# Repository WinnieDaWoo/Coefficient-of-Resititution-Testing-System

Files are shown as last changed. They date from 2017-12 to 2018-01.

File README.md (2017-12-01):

# A Coefficient of Restitution Testing System for Baseballs

The central task of this project was to design and construct a system to reliably and accurately determine the COR of a baseball with a piece of wood as a function of the relative velocity between the two bodies. This system was designed as part of an interdisciplinary one month CAPSTONE project.

An air cannon, optical laser gate, collision tube assembly was created to determine the coefficient of restitution (CoR) between a baseball and a piece of wood as a function of the relative velocity between the two bodies. A PVC compressed air cannon rated for 120 psi accelerated a baseball to speeds nearing 70 mph, and an optical laser gate captured the speed of the baseball before and after a collision with a piece of wood (ash or pine). The collision was facilitated by a collision tube racked at the end of the cannon barrel. Values for COR from baseball to baseball were consistent to within plus or minus 0.4 at various inbound velocities between 20 and 70 mph. The COR appeared to decrease as the inbound velocity increased. However, not enough data were collected to confidently apply a mathematical model to relate the two quantities. The coefficient of determination for two attempted linear fits were 0.59 and 0.78.

by Adam Woo, Dana Wensberg

## Hardware

Here is a list of the selected hardware:

### Speed Gate
| Component | Model | Description | Price |
| --- | --- | --- | --- |
| Microcontroller | [DFRobot Romeo Board](https://www.dfrobot.com/product-844.html) | The Romeo board is a microcontroller based on the ATmega32u4 chip, like the Arduino Leonardo. While the Romeo board was designed for robotics, the only special features used of this board were the built in buttons to control the system. This board was a loan from the Trinity College Engineering Department. | $0 (Retail: ~$35) |
| LCD | [DFR0063](https://www.dfrobot.com/product-135.html) | This I2C 16x2 Arduino LCD Screen is using an I2C communication interface. It means it only needs 4 pins for the LCD display: VCC, GND, SDA, SCL. It will saves at least 4 digital / analog pins on Arduino. This component was a loan from the Trinity College Engineering Department. | $0 (Retail: ~$35) |
| Lasers |  [6x Generic 650nm 5V Diode Lasers](http://amzn.to/2hCx2co) | Any 5V laser could be used for this project. These were chosen because of their small form factor and cheap price. | ~$3.50 |
| Photodiodes | [6x Generic 5MM Photodiode](http://amzn.to/2zOcfr7) | Photodiodes provide a faster response time than photosensitive resistors or transistors. | ~$1.50 |

### Air Cannon
| Component | Part | Description | Price |
| --- | --- | --- | --- |
| Cannon Materials | Schedule 40 PVC | Rated for high psi and inexpensive | ~$20 |
| Adhesives | Oatey PVC Cement | Adhesive rated for 120 psi. This adhesive was a loan from the Trinity College Engineering Department. | ~$0 |
| Quick Release | Irritrol 205TF 1” Glove valve and a Neiko 31112 Air Blow Gun Oversized Trigger | To create the quick release valve, we modified a sprinkler solenoid valve. Instructions can be read in the report | ~$32.50 |
| Testing Surface | Ash Wood | A custom cut block of ash was used as a testing surface to mimic the materials used in baseball bats | ~$10 |
| Pump | Generic Bike Pump | Any bike pump with a standard schrader valve will fit our system | ~$20 |

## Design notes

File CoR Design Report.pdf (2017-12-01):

### An Air Cannon, Laser-Gate System to Determine the Coefficient Of Restitution of

### a Baseball

Adam Woo, Dana Wensberg

Capstone I: ENGR 483
Professor Mertens and Professor Fixel October 12th, 2017

Abstract- An air cannon, optical laser gate, collision tube assembly was created to determine the coefficient of restitution (COR) between a baseball and a piece of wood as a function of the relative velocity between the two bodies. A PVC compressed air cannon rated for 120 psi accelerated a baseball to speeds nearing 70 mph, and an optical laser gate captured the speed of the baseball before and after a collision with a piece of wood (ash or pine). The collision was facilitated by a collision tube racked at the end of the cannon barrel. Values for COR from baseball to baseball were consistent to within plus or minus 0.4 at various inbound velocities between 20 and 70 mph. The COR appeared to decrease as the inbound velocity increased. However, not enough data were collected to confidently apply a mathematical model to relate the two quantities. The coefficient of determination for two attempted linear fits were 0.59 and 0.78.

Table of Contents

I. | Project | Description

The coefficient of restitution (COR) is a ratio between the energy of a system before and after a

collision. In a two body collision, if one body is fixed throughout the interaction and energy in the form of

spin can be ignored, the COR can be expressed as the square root of the ratio of the final velocity over the

initial velocity of the moving body. When a moving ball collides with a stationary surface, the ball will

rebound with a fraction of the energy that it started with. The central task of this project was to design and

construct a system to reliably and accurately determine the COR of a baseball with a piece of wood as a

function of the relative velocity between the two bodies.

II. | Presentation | of | Final | Design

It is often useful to present the final design first, allowing for specific and direct reference to the

actual system when exploring design alternatives and problem evaluation. This section will detail the final

implemented design of the system as well as describe how the subsystems work and interact with each

other. Below, in Fig. 1, is an image of the system in its entirety.

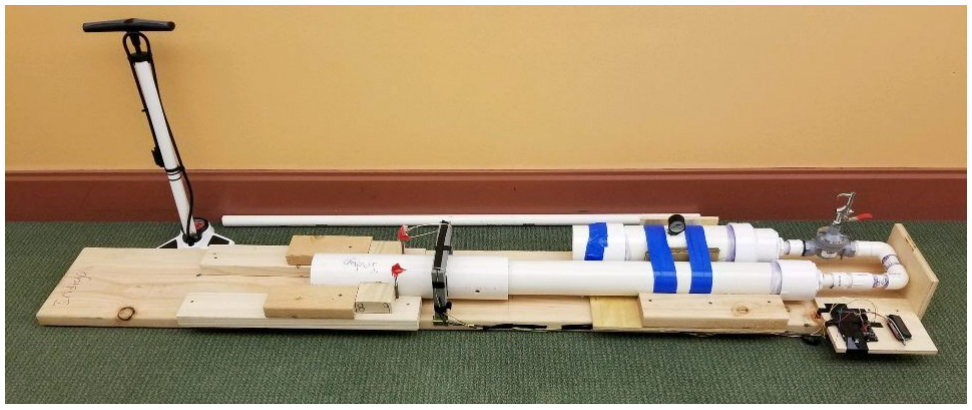
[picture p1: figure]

Figure 1. Final implemented design.

As seen above in Fig. 1, there are four main pieces to our system. There is the PVC air cannon,

the laser-gate system, the collision tube and rack, and the overall frame to the design. These sections will

be discussed separately, although none of them were designed or constructed independently, as the

elegant organization of our system seen in Fig. 1 suggests.

The pvc air cannon acts as the agent of acceleration for the baseball to establish a relative velocity

between the baseball and the piece of wood (which is housed in the collision tube). Below in Fig. 2 is a

close up image of the air cannon.

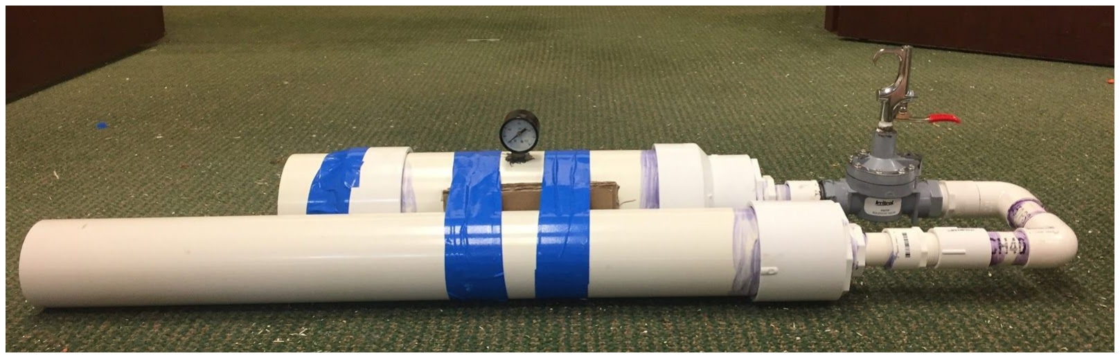
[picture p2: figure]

Figure 2. The pvc air cannon. Consists of three sections: the pressure chamber, the quick release trigger,

and the barrel.

The air cannon works in a very simple manner. The pressure chamber is pumped with air to high

pressures, and upon pulling the quick release valve, the large differential pressure between the chamber

and the barrel forces a wave of fast moving air to force the baseball out of the barrel at high speeds. The

compressed air provides an impulse to the baseball as it propagates down the length of the barrel. The

highest delivered speed we measured for the air cannon was 68 mph at a chamber pressure of 100 psi. We did not find consistent speeds for psi values lower than 40, but at 40 psi the delivered speed ranged

between 20-25 mph.

The barrel is quite simple, and does not require much additional explanation. The barrel is 3

inches in diameter, which fits a baseball (with a diameter of about 2.94 inches) tight enough for consistent

speeds when firing. It is also worth mentioning that the barrel is mounted to the pipe bend seen in Fig. 2

with a threaded connection. This threaded connection makes it very convenient to remove and exchange

the barrel with other barrels, allowing this cannon to be used for projectiles of different calibers and also

with barrels of different lengths.

The bend itself in the air cannon also serves two purposes as well that enhance the overall design

of the cannon. The bend reduced the overall length profile of the cannon, making it easier to move and

handle. Additionally, the bend and the introduction of the small slits of cardboard between the chamber

and the barrel seen in Fig. 2 ensure that the quick release valve and all connections between the chamber

and barrel do not experience any mechanical stress when lifting or moving the cannon. This feature of the

cannon is critical for ensuring its longevity and reliability. All of the seals under high pressure are ensured

using high strength JB Weld epoxy. This epoxy is excellent for withstanding high static pressures, but the

epoxy fails very easily if a shear or bending stress is applied to it. The bend and cardboard slits in concert

with the taped connection ensure a comfortable seating of the chamber to the barrel, allowing for

stress-free movement of the cannon. We utilize the ease of moving the cannon around as well as its

reduced length later on in our design when designing our mounting system.

The pressure chamber is a length of 4 inch diameter schedule 40 PVC pipe fitted with an endcap,

a Schrader valve, a pressure gauge, and a series of connections to fit to a one inch diameter PVC threaded

connection. Seen below in Fig. 3 is a close up of the Schrader valve connection as well as a portrait

profile along the length of the cannon.

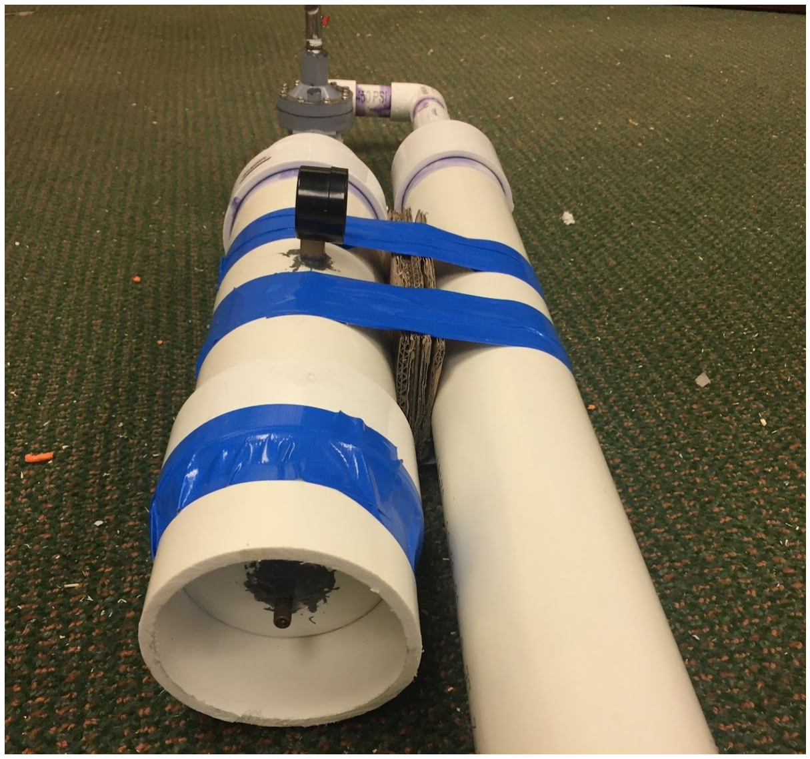
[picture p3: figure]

Figure 3. Portrait profile of the cannon. The Schrader valve connection can be seen in detail towards the

bottom left.

As seen above in Fig 3. A Schrader valve connection, the typical connection used for bike and car

tires, was fitted to the endcap through a drilled hole and sealed using JB Weld epoxy. Another section of 4

inch diameter PVC pipe was glued and taped onto the end to protect the valve from experiencing any

mechanical stress from bumping into the ground or wall when being moved around. Fig. 3 also demonstrates the effectiveness of the cardboard slits and connecting tape to seat the chamber and barrel to

one another. The 4 inch PVC pipe was rated for 120 psi, while all the JB Weld connections were rated for

200+ psi.

To create the quick release valve, we modified a sprinkler solenoid valve. A close up of the valve

can be seen below in Fig. 4.

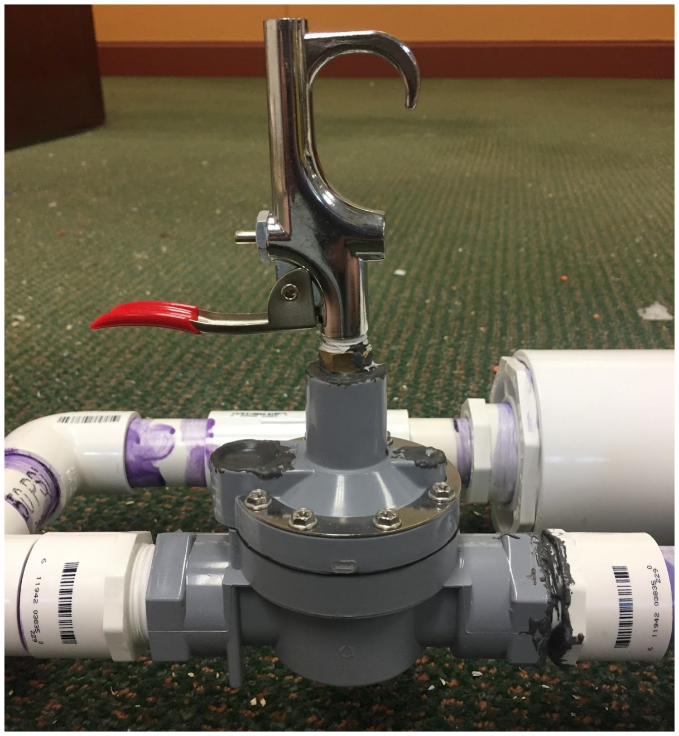
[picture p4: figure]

Figure 4. Close up of quick release valve. Modified from an Irritrol 205TF 1” Glove valve and a Neiko

31112 Air Blow Gun Oversized Trigger.

To explain how the quick release valve works, we will refer to the diagram below in Fig. 5.

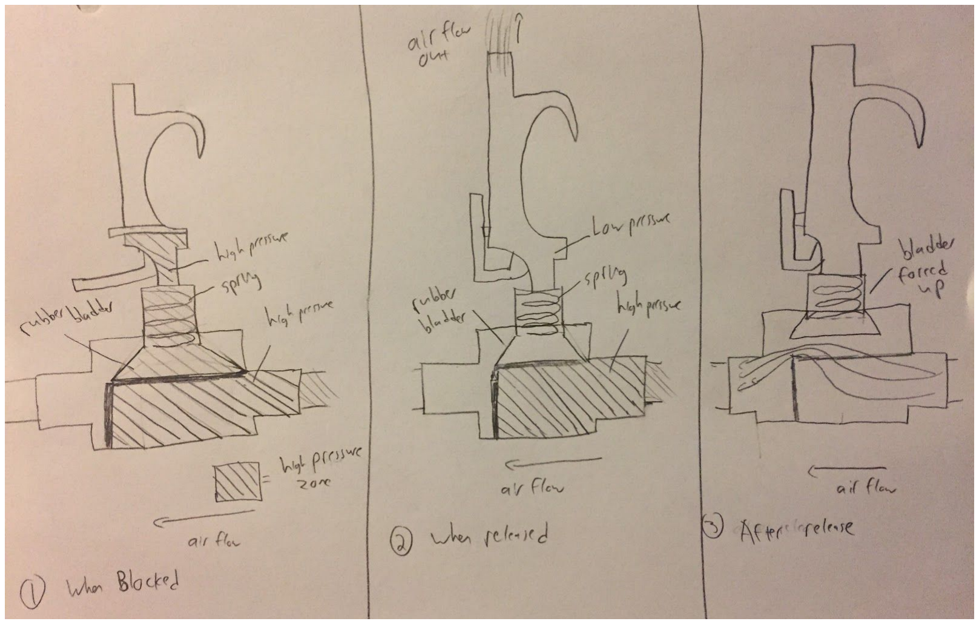
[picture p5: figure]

Figure 5. Three-phase diagram explaining the quick release mechanism.

The modified sprinkler valve has a compressed spring that pushes down on a rubber bladder that

forces a seal between the high pressure zone upstream (denoted by areas with diagonal lines) and the low

pressure zone downstream. At the top of this rubber bladder is a small hole that allows the volume

directly above the bladder to also pressurize to the same pressure as inside the pressure chamber. The way

the blow gun trigger works is that in the down position, there is a small piece that blocks airflow to the

atmosphere out of the top of the trigger. When in the up position, this small piece moves, and allows air to flow through the trigger piece to the atmosphere. As seen in Fig. 5, at stage 1, both the volume above and

below the rubber bladder are pressurized at the chamber pressure. In stage 2, once the blow gun trigger is

pulled to the up position, the small amount of air at high pressure within the trigger quickly flows out of

the top of the trigger piece. Then in stage 3 there is a very large pressure differential above and below the

rubber bladder. With a very high pressure below the bladder and a low pressure above the bladder, the

bladder is forced up, breaking the seal, allowing the compressed air from the chamber to flow through to

the barrel very quickly. This quick flow of compressed air is what provides the impulse to the baseball

and accelerates it. The sprinkler valve was originally fitted with a solenoid switch, but we found that the

switch did not work well or quickly enough to provide the desired impulse to the baseball at higher

pressures.

This quick release mechanism proved to be very reliable and very safe as well. The quick release

trigger was rated to more than 300 psi, and the JB Weld in concert with teflon tape created very sturdy

high pressure seals for confident operation. This simple trigger allows for very easy use of the gun, and

does not require nearly any physical exertion on the part of the user. This design allows for very

straightforward point and shoot operation. There was however one notable drawback to this trigger

mechanism. To the lift the bladder and allow the compressed air to flow from the chamber to the barrel,

we found that a minimum of a 12 psi pressure difference was required. As a result of this requirement,

after firing the cannon, around 12 psi would always remain in the chamber. This means that not all of the

air from the chamber was delivered to the baseball upon pulling the trigger.. As the ball propagates down

the barrel, the pressurized air behind it is expanding, losing its pressure as it grows to fill more volume.

With less total air being pushed behind the ball, that pressure will drop quicker, resulting in a smaller total

delivered impulse to the baseball, and thus a smaller exit velocity. This tradeoff in speed however was

compensated for with the increased ease of use and safety the trigger mechanism provided.

The next major sub system to our final design was the laser-gate system. We used a laser-gate in

concert with an DFRobot Romeo to measure the speed of the ball both before and after the collision.

Pictured below is our laser system implemented in our final design.

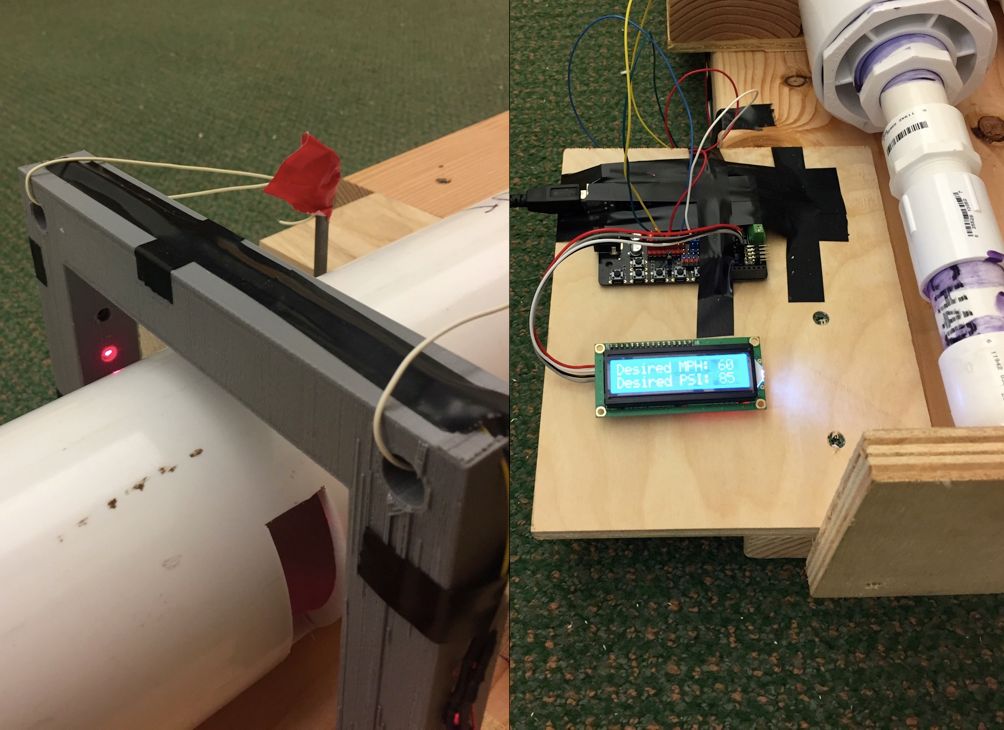
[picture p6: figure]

Figure 6. Implemented laser gate and microcontroller/lcd system. Used to measure the pre and

post-collision speeds and calculate the COR.

As seen in Fig. 6, the laser-gate system was mounted to peer through a slit in the collision tube,

and the microcontroller/lcd system was mounted on a platform next to the release trigger. Our laser-gate

system consisted of three laser diodes incident on three photoresistors wired in series with one another.

These three lasers were mounted inside of a 3D-printed rectangular gate, printed to form a perfect plane

for the baseball to pass through. Using a plane of lasers instead of a single laser ensures we capture the entire diameter of the ball as it passes through our gate. Using one laser introduces the risk of only

capturing a fraction of the baseball’s diameter as it breaks the laser, since the cross-sectional thickness of

a sphere is smaller as you move toward the top and bottom of the object. The signal output of the three

photoresistors was routed to an Arduino Romeo microcontroller. Upon the lasers being broken, the

voltage output from the photoresistors increases significantly. The microcontroller records when these

large steps occur. The time difference between these drastic steps is then compared to the diameter of the

object to calculate the speed of the object. This method relies on a consistent value for the diameter of a

baseball. The diameter of a baseball is listed as varying from 2.86 in to 2.94 in, which is a spread of plus

or minus 1.4 % from the average value of 2.9 in. Due to this uncertainty, we can expect our values for

inbound and outbound speed to have at least an uncertainty of 1.4%. Due to the capture rate of the

microcontroller, the actual percentage of uncertainty is likely to be larger. After collecting the speeds

before and after the collision, the microcontroller calculates the COR and displays the speed and COR

information on the LCD for the user.

The next major piece of the design to explore, and perhaps the most important and most clever, is

the collision tube and rack. The collision tube in our system does many things at once, and makes the

system very easy and safe to use. Below is a picture of the unmounted, unracked collision tube.

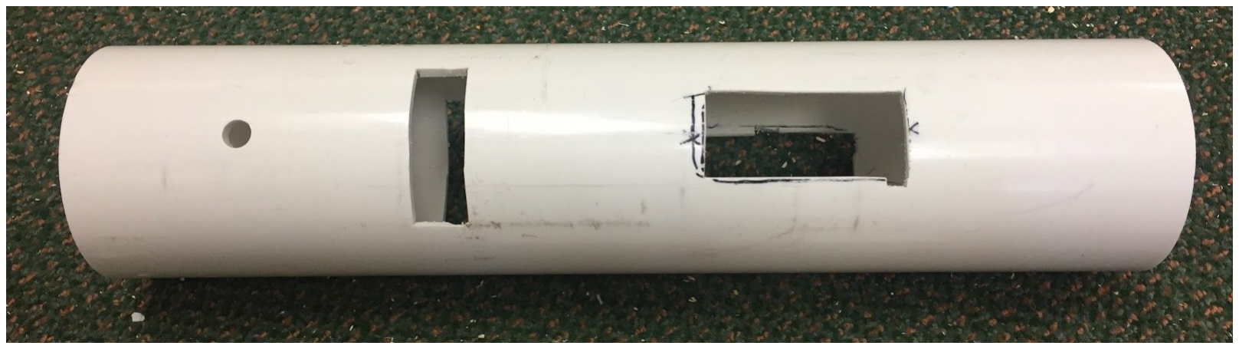
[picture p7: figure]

Figure 7. Collision tube. Holes described from right to left: 2”x4” wood sample slot, laser-gate slot,

optional secondary laser hole.

The collision tube is a piece of 4 inch PVC pipe cut with three slots that serve different and very

important purposes. There is a slot for inserting the piece of wood for the collision, a slot to allow the

laser-gate to peer through, and an additional third slot for another laser if we wanted to implemented

another speed measurement system that utilized a fixed distance step. The essential other piece to the

collision tube is the rack that it fits into. The collision tube rack is shown below in Fig. 8.

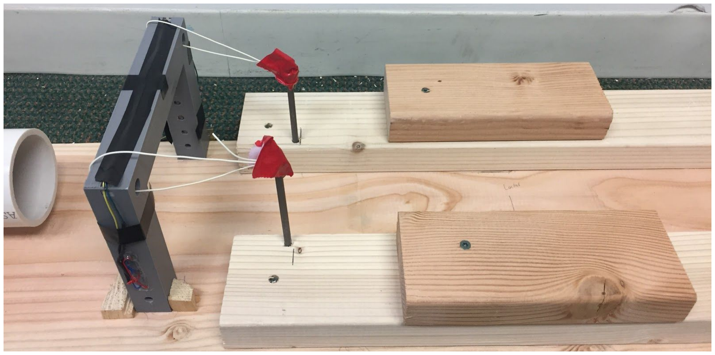
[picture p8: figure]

Figure 8. Collision tube rack.

The collision tube rack is responsible for holding the collision tube in place during testing. The

openness of the collision tube rack design allows for complete freedom of the collision tube, making

reloading very easy, safe, and convenient. The way the collision tube and rack work in concert is very

simple but also very effective. First, a standard 2”x4” piece of wood is inserted into the horizontal slot of

the collision tube. The user then rests this piece across the upper two pieces of wood while pointing the

collision tube through the rectangular laser-gate. Fig. 9 below shows step one.

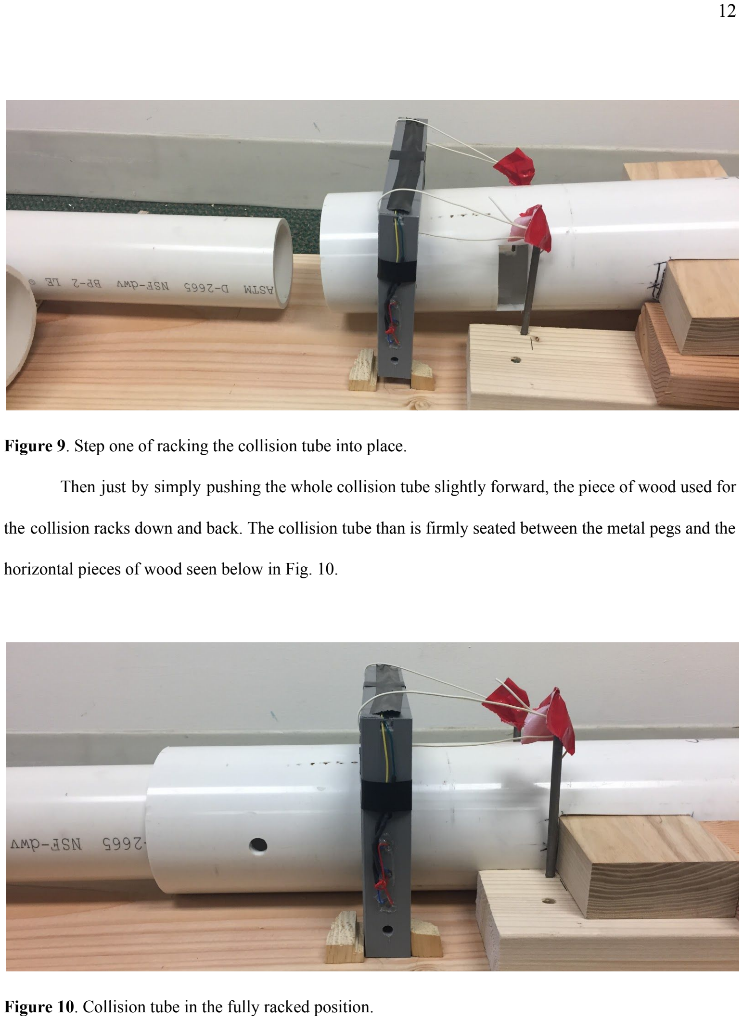
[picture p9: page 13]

Figure | 9. Step one of racking the collision tube into place.
| Then just by simply pushing the whole collision tube slightly forward, the piece of wood used for

the collision racks down and back. The collision tube than is firmly seated between the metal pegs and the

horizontal pieces of wood seen below in Fig. 10.

Figure 10. Collision tube in the fully racked position.

In this fully racked position, the collision tube mates perfectly with laser gate and the barrel of the

gun. The gun barrel lies nearly perfectly coradial with the collision tube in this position, ensuring a nearly

head perpendicular collision with the piece of wood. Fig. 11 below illustrates how the laser-gate peers

perfectly through the center vertical slot of the collision tube when fully racked.

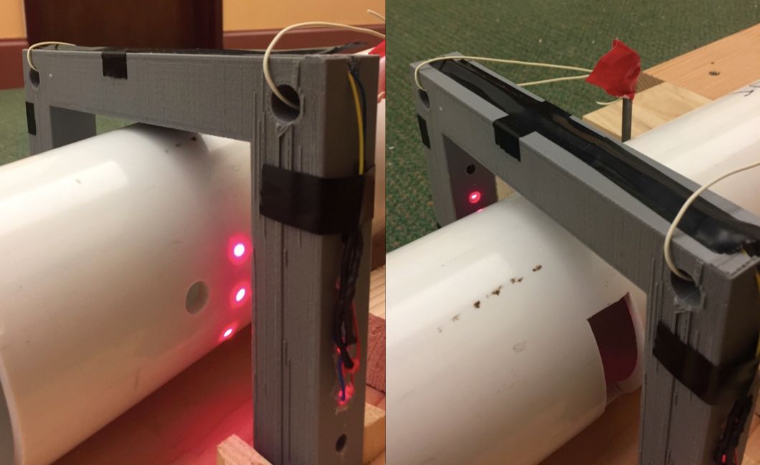
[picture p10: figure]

Figure 11. Demonstration of how racking mechanism and slot in collision tube enables the laser gate to

function properly when in fully racked position.

The collision tube and its racking system also creates a perfectly safe environment for testing.

When fully racked, the barrel end is covered by the collision tube, and the collision tube exit is

completely blocked by the piece of wood, but still allows for air to easily flow around it. There is no

physical way for the ball to escape the system when firing, making it exceedingly safe to use.

Additionally, as the collision tube is completely removable, the gun can be reloaded easily without having

to move the gun. Fig. 12 below illustrates how the collision tube blocks the exit of the ball, but allows for

excellent airflow through the barrel of the gun, and how the system is reloaded.

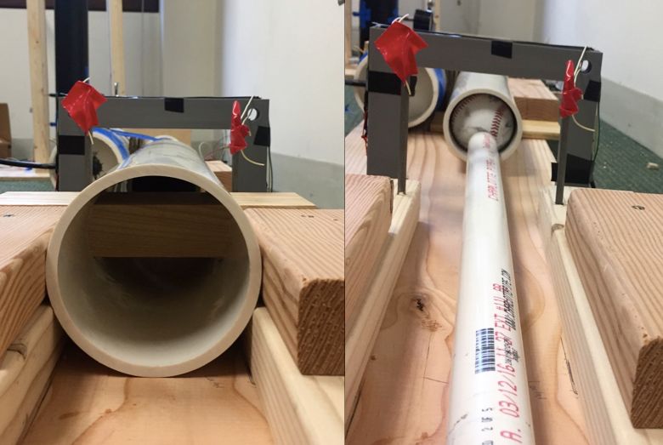
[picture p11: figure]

Figure 12. Back of collision tube when racked, and reloading process.

The collision tube and rack are most likely the two most unique elements to our design. Together

they simplify the design immensely and allow for easier implementation of other pieces of the system,

such as measuring the energy of the system after the collision. The collision tube allows for enough space

for convenient airflow and reloading, while also keeping the collision confined so as to only require the

use of one laser-gate. The collision tube is also quite small in length, which minimizes the impact gravity

has on the path of the ball. This system also allows us to conveniently test different types of wood for very low cost. The typical 2”x4” is manufactured in nearly every type of wood as the standard size used

for building, so viable test pieces are very easy to obtain. The racking system also removes much of the

possibility for user error. Our system does not require the user to line anything up or be careful with any

aspect of the setup. Everything simply fits together as it should, and all the user has to do is pump up the

chamber and pull the trigger.

The final piece of the design to discuss is the mounting of all of the subsystems into one

contained unit. The mounting process for the gun and rack was performed at the same time, and the

mounting process for the laser gate and the microcontroller was performed somewhat iteratively

afterwards. As seen in previous figures, the entire system was mounted on a single 10 ft piece of pine.

Below in Fig. 13 is the mounting section for the PVC air cannon.

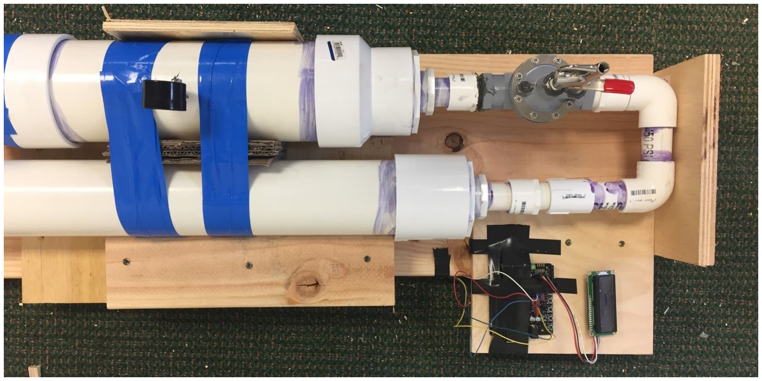
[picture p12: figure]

Figure 13. Mounting section for the PVC air cannon and microcontroller/LCD.

There are five features to notice from Fig. 13. The first and least important/impressive feature is

the mount for the microcontroller and the LCD. This platform provides a sturdy location for the user to interact with the laser gate and view the outputs of the electrical system. The second aspect to notice is the

piece of plywood on the end of the base. This piece of wood racks the gun lengthwise along the base,

ensuring that the kickback from firing the air cannon does not displace the cannon in the backwards

direction for the next trial. The third important aspect to discuss is the piece of plywood attached along

the the top of the base. This piece of plywood racks the cannon widthwise along the base by making

contact along the length of the pressure chamber. The fourth aspect to notice is the 2x4 piece of pine that

lies incident along the barrel. This piece of wood serves two purposes. The first is it racks the cannon

widthwise along the base, but it also mates perfectly with the 3 inch transition piece at the base of the

barrel. This small detail racks the cannon lengthwise along the cannon in the forward direction. This last

piece of wood prevents the cannon from moving in the positive and negative x and y directions, while still

allowing the gun to be picked up and removed from the base at any time. The final feature to notice from

Fig. 13 is the piece of plywood beneath the pine 2x4. A close up of this feature is given below in Fig. 14.

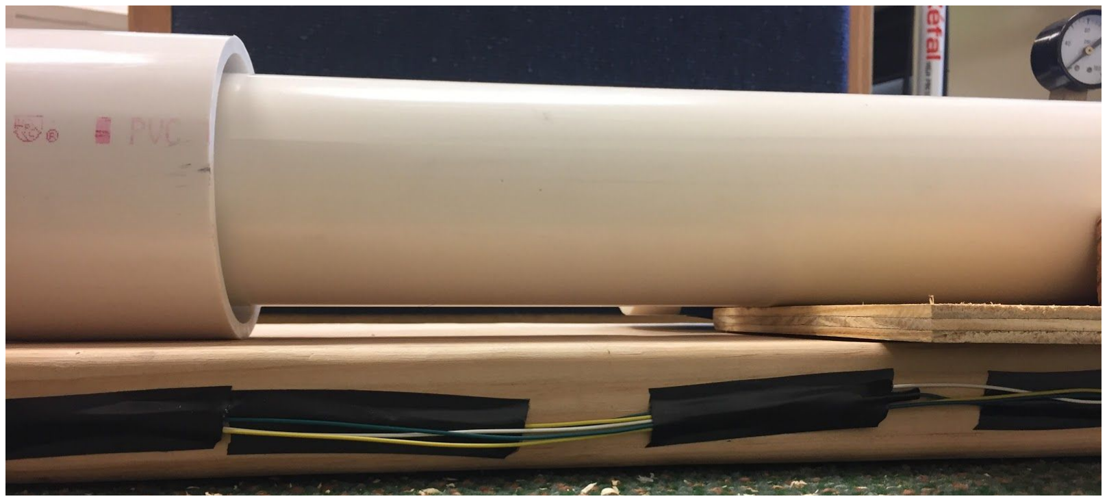
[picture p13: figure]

Figure 14. Plywood piece on base that mates the barrel to the collision tube at proper height.

As seen above in Fig. 14, this last piece sets the height of the barrel to be nearly perfectly coradial

with the collision tube, ensuring that upon entry, the baseball will not hit any of the walls of the collision

tube and introduce inaccuracies into our COR or speed measurements. After completing the mounting of

the air cannon, the mounting for the racking system was implemented to make the collision tube coradial

with the barrel of the gun, as I discussed when explaining the collision tube and rack system.

The mounting system for the laser gate was adjusted slightly as we tested. The primary mount

was the 3D-printed frame as we discussed previously. However, other important aspects we neglected to

mention were the introduction of the hinge, small wood racks, and tension wires. Below in Fig. 15, we

present the opposite side of the laser gate frame, showing the hinge.

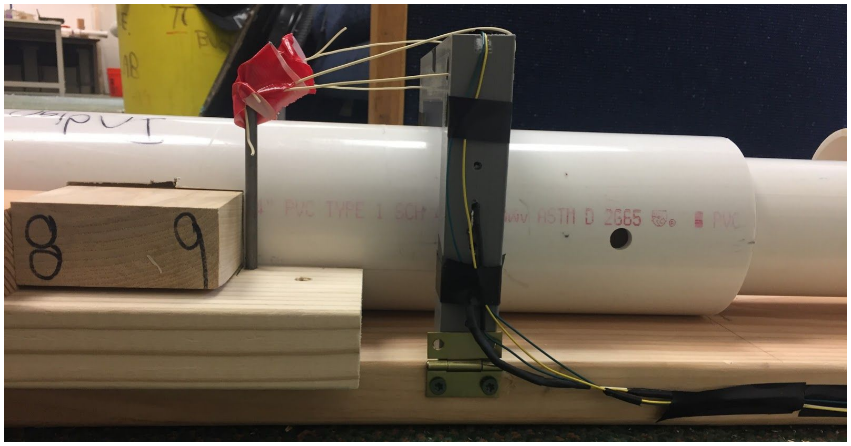
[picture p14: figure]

Figure 15. Laser gate frame hinge allowing for smooth removal and racking of the collision tube.

We introduced the hinge because we found when removing and racking in the collision tube, the

laser gate frame was slightly too short to allow for smooth and natural movement. As a result of this discovery, we needed to have the frame free to move, even if only slightly, in the z-direction (up from the

base). The hinge was the perfect solution to this problem, and also provided a solid way to connect the

gate to the base. The hinge in concert with the small wood racks and the tension wires presented a perfect

solution to our laser gate mounting problem.

The small wood racks and tension wires can be seen in Fig. 10. These small pieces serve to

ensure the laser gate is perpendicular to the collision tube with every trial. They remove the need for the

user to align the lasers with each trial and help to keep the lasers steady after a collision. The tension

wires prevent the 3D-printed frame from recoiling after a collision occurred inside the tube. Especially at

higher impact speeds (greater than 50 mph) and impacts with harder woods (ash compared to pine), the

entire system experiences a significant jolt after impact. This jolt frequently caused the lasers to be broken

by the collision tube itself since the frame would displace so violently after the collision. The introduction

of these tension wires solved this problem beautifully without needing to introduce any complicated new

features, and still allowed for enough freedom of motion for the frame to accomplish smooth raking and

removal of the collision tube.

Our design was successful in delivering consistent COR values for two different types of wood

across a range of different speeds. Although the end product we would consider a success, there are many

ways in which the system could have failed and in fact did fall short. We will explore these scenarios and

instances now in our failure analysis.

III. | Failure | Analysis | and | Assignment | of | Uncertainty

When performing failure analysis, it is important to remember exactly what the goals of the

system are. Referring back to our problem statement, we needed to deliver a “system to reliably and

accurately determine the COR of a baseball with a piece of wood as a function of the relative velocity

between the two bodies.” We can therefore define failure as anything that prevents us from delivering such a system. In our minds there are two ways in which we can fail. There is failure by catastrophe,

where our system is either not safe or can not consistently yield values for the COR, and there is failure

by inaccuracy, where our presented values for the COR are riddled with systematic error. We will first

explore the possibility for catastrophic failure in our system, and then accuracy driven failure.

We have collected the following instances to analyze that in our minds constitute catastrophic

failure: system self-destruction, seal failure, and data-collection failure. The first thing we acknowledged

was that we would have compressed air under high pressure within our system. Amongst all the pieces

that would need to sustain prolonged high pressure, the pressure rating on the 4 inch PVC pipe was the

lowest at 120 psi. We never enacted a block in the system (either mechanical with a relief valve or

electrical by cutting current to a pump) that could prevent the user from pressurizing the chamber above

this rating, but we figured that simply telling the user that he or she should not exceed 100-110 psi would

suffice for prototype purposes.

Seal failure was a more pervasive problem we needed to account for. A failure in a seal would

prevent the air cannon from achieving high enough chamber pressures to propel the ball at meaningful

speeds (greater than 20 mph) or even propel the ball at all (due to the rubber bladder needing at least 12

psi pressure differential to release). As we mentioned in our design presentation section, the primary agent

for ensuring our most important seals (around the Schrader valve, around the pressure gauge, and the

ports of the modified sprinkler valve) was JB Weld. JB Weld fails quickly under shear or bending loads.

To prevent failure at the fill valve and the quick release valve, we introduced the end cap cover and the

bend as we have discussed prior. However, the pressure gauge remained exposed even in our final design,

and if it were to be bumped or the cannon were dropped on the gauge, the JB Weld seal likely would have

broken. Although a repair on the seal is simple, high strength epoxy takes 24 hours to set, so a seal break

on performance day would indeed constitute complete catastrophic failure. As the cannon would be set up

in its racked position as seen in Fig. 13, we assumed that the pressure gauge would be safe from violent bumps or drops come performance time. However, a better design would include a more protected

pressure gauge.

The final possibility for catastrophic failure we identified was data-collection failure. This groups

together many potential electrical and mechanical problems. We did our best to combat electrical failure

by ensuring our component input and output voltage ranges were correct, and any and all electrical pieces,

like the wires, microcontroller, and LCD, were all fastened down in a mechanically stable way. The most

likely failure possibilities we envisioned with data collection had to do with aiming accuracy and object

interference. The introduction of the collision tube and our racking system essentially prevented any

potential failure with the ball not passing through the laser-gate plane, so aiming accuracy was of

negligible concern come demo day. However, object interference, as in something other than the baseball

tripping our laser gate, proved to be a more pervasive failure possibility we needed to account for. Due to

the jolt caused by the collision between the baseball and the piece of wood, there were two things that

could cause object interference. The first is that the collision tube itself would rebound after the collision

and move as far as to rest in front of the lasers, preventing any sort of accurate measurement. The second

is the frame holding the laser gate would jolt violently towards the air cannon barrel, as its inertia wants to

keep it from accelerating. To combat these two problems, we iteratively made one modification to the

collision tube and introduced two features to the system. First, we made the viewing slit on the collision

tube much wider, allowing for more wiggle room for the lasers to peer through to their respective

photoresistors. Secondly, we introduced the metal pegs in the wood to prevent the collision tube from

sliding forward after the collision. Thirdly, we introduced the small wooden racks for the frame and the

tension wires to prevent the frame from jolting so severely. With the introduction of these features, we

experienced excellent data collection consistency for collisions between speeds of 20 mph and 65 mph,

our target range.

Accuracy driven failure analysis is a much more rigorous and thought intensive process than

catastrophic failure analysis. We will begin our accuracy failure analysis with a discussion of our

assumptions. To deliver a perfectly accurate value of COR, our system assumes the following:

1. Every baseball has a diameter of 73.7 mm (2.90 in)
2. Our energy balance boundary conditions:
a. Kinetic energy of piece of wood is 0 before and after collision
b. Gravitational potential energy of all bodies are the same before and after collision
c. Rotational energy of the ball (spin) is 0 before and after collision
3. The baseball passes through the laser gate plane in the same orientation before and after

the collision (related to the no spin assumption)

4. The plane of the laser gate is perfectly normal to the path of the ball before and after the

collision

5. Air resistance is negligible over the course of the collision measurement times
6. Infinitely fast sampling rate

These assumptions are presented in order of difficulty of analysis, and will be analyzed in the order

presented. While all of these assumptions are incorrect, we will analyze how much effect they could

potentially have on our measurement outcomes.

As we have mentioned, baseballs have listed diameter ranges of 2.86-2.94 in, and are not uniform

spheres. This assumption will automatically insert an uncertainty of +/- 1.4% into our velocity

measurements, and +/- 2% into our COR value due to the combination of uncertainty of pre and post

collision measurements.

The second assumption is equally easy to determine incorrect but much more difficult to quantify.

The way we measure the COR is by comparing the velocity of the ball after the collision to the velocity

before the collision. This is only viable when making the boundary condition assumptions listed for number 2 above. The conditions spelled out in 2a are the easiest to analyze. The piece of wood is at rest

prior to the collision, but after the collision the wood has a few millimeters of space to move before it is

stopped by the metal pegs seen in Fig. 15. During testing, we observed the block of wood and the whole

collision tube actually move these few millimeters in response to the collision. As a result we cannot

assume the kinetic energy of the block after the collision is 0. However, as we have no way to quantify

this amount of energy, we cannot provide a numerical analysis and only a heuristic application of

uncertainty. We will assign an additional 2% of uncertainty to our COR measurements due to this

rebounding effect.

The conditions given by 2c also cannot be quantified consistently. In our system, the baseball is

not stuffed into the barrel with any sort of wrapping material. As a result, it is likely rolling or touching

the surface of the barrel at some point along its journey out of the barrel. Similarly, inside the collision

tube, both before and after the collision, if the ball were to touch the sides of the tube, additional

rotational impulses would be applied to the baseball by friction. Also, the collision itself could induce

spin on the ball. As a result of these realities, the assumption that the ball has no spin before and after the

collision is almost certainly false. However, when observing high speed video of baseballs being shot out

of air cannons, similarly without any wrapping material, there is very little spin on the ball (1).

Additionally, perpendicular collisions (or nearly perpendicular collisions) with static objects do not tend

to add significant spin energy to baseballs. In fact, they tend to reduce overall spin significantly (2). To

attempt to apply any sort of numerical uncertainty, let us look into some aspects of spin with baseballs.

According to resource 3, the spin rate on fastballs appears to reduce somewhat linearly with speed of the

ball. For one observed pitcher, an 80 mph fastball had a 2000 RPM spin rate, where a 60 mph fastball had

a 1500 RPM spin rate. Since our air cannon can shoot 60 mph, and we observed that spin out of an air

cannon is typically very small, let’s analyze the following “worst case” situation for our no spin

assumption:

1. KE for the block of wood is 0 before and after collision
2. No changes in PE for any body involved in collision
3. Ball inbound velocity is 60 mph with 750 RPM spin rate (half that of a pitched ball)
4. Ball post-collision velocity is 30 mph with 0 RPM spin rate
5. Approximate the ball as a solid sphere, with a radius of 1.45 in

Performing the energy balance for the spin and no spin cases yields the following relationships for COR.

We first must centralize our units:

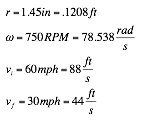
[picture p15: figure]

After performing calculations, the COR with spin, or our “worst case”, is 0.499. The COR for the no spin

case, or what we assume in our system, is 0.50. So even in this absolute worst case scenario, the COR is

only affected by 1%. This percentage is significant, but not large enough to constitute an assignment of

failure, even in the worst possible case. Moving forward, we will assume the worst, and apply a 1%

uncertainty due to spin considerations for values of COR.

Now to consider the assumptions given by 2b, where the gravitational potential energy of all

bodies are the same before and after a collision. Let us again look at a worst case scenario for this

assumption. The slowest speed that we have reliable tests with is around 20 mph. The maximum possible

change in height of the ball from before the collision to afterwards refers to the scenario where initially

the ball is touching the top of the collision tube, and afterwards the ball is touching the bottom of the

collision tube. For a 4 inch diameter collision tube and a 2.9 inch diameter baseball, this means the

maximum change in height is 1.1 inch. For this worst case scenario, let us also assume the ball never

spins, and that the rebound velocity is 10 mph.

For our worst case, with the height change, the COR is 0.499999, as compared to 0.50 when ignoring

height changes. As this calculation demonstrates, changes in height have a negligible effect on the

outcome COR.

Assumption three is related to the idea of spin and the type of baseball being used. A flat seam

baseball has seams raised 0.031 inches from the spherical surface of the ball. High seam baseballs are the

more traditional kind, and their seams are raised 0.048 inches from the surface of the baseball, giving it a

larger radius at certain locations (4). For this analysis, let us assume we are using a high seam baseball. In

the scenario where the baseball passes the laser gate along its largest width before the collision, and

passes the laser gate along its thinnest width after the collision, let us calculate how much effect this will have on the COR assuming all other assumptions are maintained. Let us use 60 mph for initial velocity

and 30 mph for the final velocity, and that the ball’s true diameter is 2.9 inches. The initial velocity

measurement is therefore overestimated, since we compared a time step to a distance of 2.9 inches as

opposed to 2.996 inches (height of seams added to either side). The true initial velocity is 58.1 mph. The

post collision velocity is true, however, since it crossed the laser gate at its true diameter of 2.9 in. So the

real values COR is 0.517, compared to the yielded value of 0.5. This is a deviation of roughly 3.3% from

the truth value. This is significant, but again, the worst case scenario is unlikely, and high seamed

baseballs are only used in certain circumstances, mostly for beginners in little league. In the mlb, they use

rolled-seam balls, which have a much lower raised height of the seams (5). As a result of these

observations, we will apply a 2% random uncertainty to compensate for assumption three.

The fourth assumption is the most geometrically interesting to analyze. An assumption like this

can overlook errors because the ball might pass through the laser gate at an angle, breaking the lasers for

longer than they would be broken given a crossing normal to the plane of the lasers. Picking out the worst

case scenario for this assumption takes a bit of thought. Let us again assume a 60 mph initial velocity

measurement and a 30 mph initial velocity measurement. Assume that the initial path of the ball is

perfectly normal to the plane of the laser gate. But for the crossing on the way back, humor a situation

depicted below in Fig. 16.

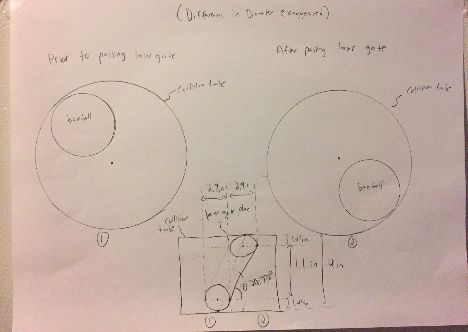
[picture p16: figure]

Figure 16. Depiction of worst case measurement scenario for assumption 4.

Although it is extremely unlikely that this physical depiction would ever actually occur, it does

represent the absolute worst case scenario where our laser system would actually record a measurement

for velocity. For a situation like this to occur, the ball would have to pass through the beam plane at an

angle of 20.772 degrees. To achieve an angle like this, a serious random deflection is required off of the

piece of wood, which would surely result in very inaccurate COR readings for reasons other than the one

currently discussed. Nonetheless, when accounting for this angle of incidence with the plane, the effective

diameter of the baseball as far as the laser gate is concerned changed from 2.9 in (the default radius) to

3.1 in, resulting in a true final velocity of 32.1 mph. After making this adjustment, the true COR is 0.535.

The outputted value would have been 0.50, which is a deviation of 6.5% from the truth value. This percentage is significant, but again, this represents a nearly impossible fringe scenario. Angles closer to 5

degrees are much more reasonable to assume, which would result in a deviation of 0.4% from truth. We

will assign an uncertainty of 1% to our values of COR due to the implications of assumption number four.

To analyze the implications of assumption five, we must look at our physical system. For air

resistance to significantly affect the value of the COR, the air drag must take a significant amount of

energy away from the ball from the time it first breaks the laser gate to when it passes the gate completely

after the collision. The laser gate is close to 4 inches from the face of the piece of wood. The ball will

experience air drag for the entire 4 inches on its way to collide with the wood. After the collision, the

opposite side of the ball with experience drag, and it will need to travel 4 inches again until it completely

breaks the laser gate. So the ball will experience a drag force for a total of 8 inches of distance, 4 inches at

the incoming velocity, and 4 inches at the rebound velocity. For these short 4 inch distance, let us assume

the velocity is constant (60 mph inbound, 30 mph rebound). Let us perform an impulse estimate to see of

a significant amount of energy is lost due to air drag over this short journey. At 60 mph, the ball traverses

4 inches in roughly 0.004 seconds. At 30 mph, the ball traverses 4 inches in roughly 0.008 seconds. We

will estimate the drag coefficient of a baseball at C=0.4. Performing an impulse estimation:

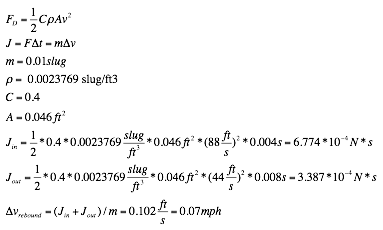
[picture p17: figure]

We see that the rebound velocity would only be reduced by about 0.07 mph. So the true measurement

speed given no drag would be 30.07 mph, resulting in a true COR of 0.501. This is a deviation of 0.23%

from the measured COR value in this scenario. So as a result, it is fair to say that air drag can be ignored.

The final assumption to analyze is the assumption of infinite sampling rate of the microcontroller.

In reality, the sampling rate of the Arduino Romeo is 9600 samples a second, meaning that information is

collected from its ports 9600 times every second. This reality most certainly will add some uncertainty to

our COR output. Let us again consider the worst case scenario with collection at the highest recorded

speed we measured, 68 mph. At 68 mph, the ball translated 2.9 inches in 0.0024 seconds. With a sampling

rate of 9600 samples per second, the Romeo board is collecting a sample every 0.000104 seconds. That

means over the course of the baseball breaking the lasers, the sample period will occur 23.27 times. But

since samples are discrete, the board can only take 23 samples, which means the board will assign a

traversal time of 23*0.000104 seconds = 0.002392 seconds compared to the real value of 0.0024 seconds.

If we imagine the worst case scenario, where the ball breaks the laser plane the instant after a sample and

leaves the plane the instant before another sample, the board will assign 22 sampling periods to the ball

traversal time. This sampling error corresponds to a maximum of +4.7% error in the inbound velocity

values. However, this is not the whole story, because on the way out, after the rebound, the ball is just as

likely to get caught in a sampling “worst case” scenario. Due to the discrete nature of sampling, both the

inbound and rebound velocities will almost always be overestimated because the board assigns a shorter

time for a traversal than what really happened. However, this overestimation is fractionally larger the

faster the ball is moving because there are fewer sampling periods over the period of traversal. Due to the

mirroring of the speed measurement inaccuracies, the COR will be affected less than the individual speed

measurements. If we are to expect a rebound velocity of 34 mph for an inbound velocity of 68 mph, and

we assume the same sample clipping effect for the rebound velocity measurement, the deviation of the

COR from the truth value is 2%. As this effect will scale with velocity, and there is usually only a single period clipping in the measurement (as opposed to two periods for the worst case scenario), we will

assign a 1% uncertainty to all COR values to compensate for assumption number six.

Now having parsed through all of our assumptions and attempted to numerically assign a

fractional error to all them, we will collect our terms and see what our overall error estimate come to. If

we assume all sources of uncertainty are random, we combine them with the least squares method.

Table | 1. Summary of assignment of uncertainty due to each assumption
Assumption | Number | Assigned Uncertainty
Universal Diameter | 1 | 2%
Wood block never moves | 2a | 2%
No change in gravitational potential energy | 2b | 0%
The baseball never spins | 2c | 1%
Identical orientations for crossing laser gate | 3 | 2%
Path of ball is always normal to plane of laser gate | 4 | 1%
Negligible Air Drag | 5 | 0%
Infinite Sampling Rate | 6 | 1%
Least Squares Total | - | 3.91% => 4%

So as seen from Table 1, the uncertainty we can attempt to quantify from our system leads to an

assignment of 4% uncertainty. There are other potential sources of uncertainty that have nothing to do

with our system, such as the inconsistency of the material properties of a baseball. Collisions are very

random events and can rarely be predicted with perfect accuracy, even in such a controlled setting.

IV. | The | Design | Story

The first step in designing an engineering solution is to identify the problem. Our task was to

develop a method of measuring the Coefficient of Restitution of a baseball against a wood surface as a

function of the relative velocity between them. With the problem defined, we moved onto problem

evaluation.

Problem Evaluation

A practical use of this information would be for the impact of the ball of a baseball bat after a

pitch. The average fastball speed in the MLB is 90.9mph with a range of 50-100mph for all pitches. The

average baseball bat is made out of hardwoods like ash, hickory, and maple and 2.61in thick at the

thickest point. Baseball dimensions fluctuate between 9.00-9.25in in circumference, 2.86-2.94in in

diameter, and 5.00-5.25 ounces in weight. The MLB does not release the COR measurements for their

baseballs, but Rodney Cross in “Physics of Baseball and Softball” writes: “Elastic behaviour in the

vertical direction is described by a number called the coefficient of restitution (COR) which is about 0.5

for a baseball, depending on ball speed.” This is verified by the UMass-Lowell Baseball Research Center

which found the COR to vary between .514 and .578 at at 70℉ and 50% relative humidity within ±5% in

relative humidity and within ±5℉ in temperature, using the ASTM wall test. The ASTM wall test uses an

air cannon to propel a baseball into a stationary piece of ash. With this information, we knew that we

wanted to design our system to establish a relative velocity between 50-100mph between the wood and

the ball, impacting against a hardwood (preferably ash) about 2.5in thick.

We also wanted the system to be easy to use, repeatable, adjustable, inexpensive, and safe. We

decided that a self contained system that displayed a high level of information and could be controlled

with minimal effort would best achieve these standards. The wood surface should be flat (perpendicular to

the direction of motion) and stationary to avoid complication with movement or angles. The method of propulsion should be adjustable in power and easy to set up. The methods of measurement should be non

interfering.

Considering Alternatives

We first ruled out most methods of mechanically measuring the inbound and outbound speeds or

displacement. Some systems we considered were a spring catching mechanism or pendulum catching

mechanism. With our limited resources, it would be difficult to create a mechanical device that could

accurately and reliably collect information on the system’s energy while also maintaining good usability

and minimizing complexity. This lead us to the decision that the system of propulsion should be decided

upon first, and then iterated upon once designing the measurement system. This was because modifying

an electrical system of measurement was much simpler than modifying a propulsion system, because of

the small and stationary nature of sensors.

There were three main methods of propulsion explored: elastic, gravitational, and pressure.

Combustion and magnetic propulsion methods were also suggested, but abandoned quickly with concerns

of safety, cost, and feasibility. Elastic propulsion would involve a series of springs or bands to propel the

ball. A ratcheting mechanism would be required to load the ball into any system with enough power to

propel the ball at the desired speeds. This idea was abandoned after considering the cost of springs or

bands with a large enough spring coefficient to propel a baseball to our desired speeds. Additionally, we

envisioned the mechanical complexity of a ratcheting mechanism would compromise safety and

simplicity to a fault. Gravitational propulsion was rejected because the height required to reach 60 mph

would be about 120 ft high, or approximately 12 stories up. It would be exceedingly difficult to maintain

any sort of accuracy or control of the system when dropping from such heights.

With all these methods considered, air pressure seemed like the best propellant. It was easy to

contain at high pressures, powerful, accessible, and low cost. Some quick calculations showed that a system of 80 psi could propel a baseball ball well over 70 mph. The standard bike pump is rated for up to

130 psi, and the 4-in schedule 40 PVC pipe in the Trinity Engineering Woodshop is rated for operation at

133 psi. Barrel length for the air cannon could be varied to control for accuracy and easy loading, and a

collision chamber could be mounted on the end to contain the ball and collision at launch. The team

agreed that this was the most effective method of propulsion for this project. Below is the quick

impulse-momentum calculation we performed to confirm the feasibility of an air cannon propelling a

baseball in our desired speed range.

Given an initial pressure of 80 psi, we conservatively assumed that the cannon would deliver an average

pressure of 10 psi to the rear of the baseball on its way through the barrel. We selected one eighth the

input pressure because the expansion of air in the barrel and also air escaping around the sides of the

barrel would drastically reduce the pressure behind the ball as it propagated. For an effective barrel length

of 2 ft, and ball moving at 60 mph, the time in the barrel is around 0.02 seconds.

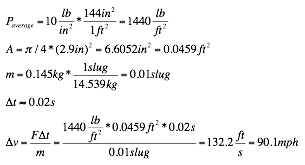
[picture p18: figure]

So at 80 psi, our most conservative estimate landed the baseball at an exit speed of 90.1 mph. Well above

our target range.

Design Iteration and Construction

The PVC was bought at Home Depot and the epoxy used for securing all the connections was

provided by the Trinity Engineering Department. The standard tire valve, called a schrader valve, was

found by visiting a series of bike shops and asking for any busted tires. Eventually, a shop cut the valve

off of an old tire tubing and it was mounted on the end of the compression chamber.

The air in the chamber needed to be released quickly and consistently in order to propel the ball at

the desired speeds. Butterfly valves were cheap and easily accessible, but difficult to open and put a lot of

strain on the system's connections. We wanted something easy to use and consistently fast. Prebuilt

solenoid quick releases were expensive, so after some research, we were able to build our own from a

sprinkler valve purchased on Amazon.com. This valve prevented 15-20 psi from escaping, but we decided

that the ease of use trade off was worth the speed loss.

Implementation of the electrical design required a method of sensing the ball, a controller to

count the allotted time the ball was in the plane, and a way of mounting the sensors to the collision tube.

Other factors to consider are time and budget constraints. A large portion of our design was contingent

around these two factors. In an effort to compensate for unexpected debugging or complications, parts

were chosen in order to begin development and testing quickly. This planning proved beneficial, as the

completion of the system early allowed us to correct for several inconsistencies and deliver an accurate

prototype on demonstration day.

A series of laser diodes and photoresistors were chosen as the sensors because of these later

factors. Other alternatives were considered, such as ultrasonic sensors, infrared emitters and receivers, and

photodiodes. Ultrasonic sensors were dismissed quickly, as they are not very precise with round surfaces

and each sensor must be individually calibrated for different distances and materials (texture and density).

Also, with the small collision tube system desired, the base detecting distance would require the sensor to

be farther away from the action than required.

IR emitters were considered because of their conic output, but dismissed because of our decision

to mount the sensors outside of the collision tube to avoid damage to the electrical system. This exposed

the sensors to other interfering light sources. A housing may have been developed to minimize

interference, but would then interfere with the loading and racking mechanisms. The IR emitters were

dismissed in lieu of other alternatives. Lasers provide a more intense, stable, and targeted light source

than IR emitters, and were used instead.

Photodiodes have a faster response time and are more sensitive than photoresistors, which would

make them better for this kind of application. However, they were not used because of time, cost, and

familiarity. The photoresistors were available from the engineering department and cost slightly less than

the photodiodes. For the estimated speeds of our mechanical system, the ~10ms sensitivity of the

photoresistor was thought to be sufficient. From testing, we found this to be correct, although after

analysis, we realize that this introduces a significant amount of uncertainty. The members of the team had

worked with photoresistors before, and had little experience with photodiodes, and therefore decided to

use the more familiar component. This was a logical error, and will be accounted for in later iterations.

Cheap laser diodes were purchased from Amazon.com (with 2-day shipping) and photoresistors

were acquired through the engineering department. This allowed us to begin building and testing our

system quickly, giving us the ability to debug well in advance of demonstration.

There are two schools of thought on laser speed gates; single point or dual point systems. A dual

point system uses two lasers or laser grids a fixed distance apart and measures the time difference

between the two points. The advantage of this system is that it can measure any object of any size. This

means that this system would remove the uncertainty of the baseball’s diameter. Despite this advantage,

we chose to use a single point system for our prototype. That is because this method was easier to

accurately implement with our limited resources.

The dual point system provides several challenges that could not be corrected with our limited

resources. First, the measurement of distance between the two points must be extremely precise. Even if

the original measurement is precise, force from the impact of the ball might shake the system, causing the

distance to vary from test to test. Second, the points must be perfectly parallel to each other. If not

perfectly parallel, the orientation of the ball as it passes through the points will cause inconsistency of

measurement. Finally, the points need to be close so that there is little space for interference from air

resistance, gravity, or other external forces. All of these challenges are solved by using a single point

system of measurement.

The alignment of the lasers matter significantly less with a single point system, and are much

easier to implement. By relying on the diameter of the ball, the system may shake or become slightly

misaligned, but still give an accurate reading for the same ball. Because the system was designed

specifically for testing baseballs, the inability to test other objects was not considered an issue. In order to

make sure the full diameter of the ball was measured every time, a laser grid system was developed.

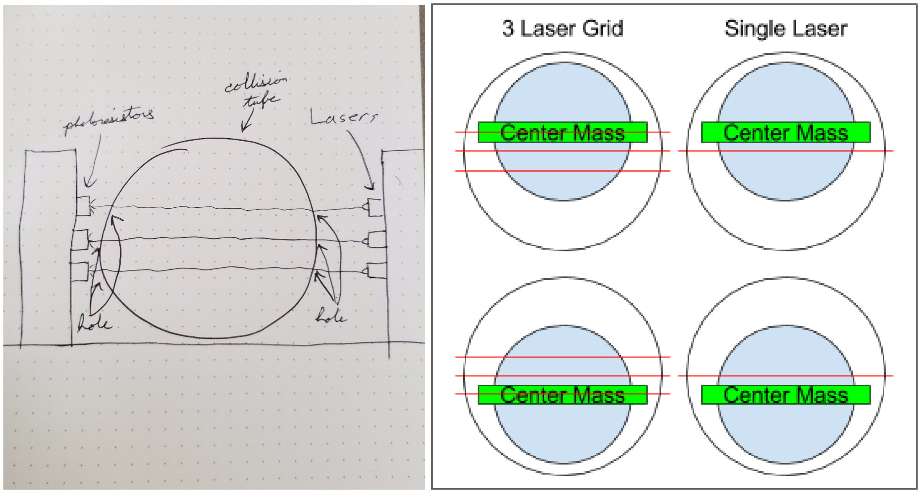
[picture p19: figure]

Figure 17. Early drafts of the speedgate system and single laser vs laser grid accuracy

The difficulty in mounting this system is that all of the lasers and resistors must be aligned

accurately with enough stability to not become misaligned. Any angles with any of the lasers would cause

inaccuracy. Although a drill press might be used to align holes, this became difficult when drilling into a

round surface at angles, as the tube or drill would slip and become misaligned. The solution was to CAD

model and 3D print a speedgate housing. Using one of the Makerbot Replicator 2s found in the Trinity

College Library, we were able to print a housing accurate to .1mm.

The DFRobot Romeo board was selected almost purely out of convenience. A microcontroller

board was the best way to develop and test the system at low cost. Other alternatives, such as building a

digital logic circuit, might be cheaper and more precise, but also significantly more difficult to design and

debug. The engineering department had several Romeo boards, as well as LCDs to work with them.

One concern we had for Arduino based boards is the limited sample rate. For a 16 MHz Arduino

the ADC clock is set to 16 MHz/128 = 125 KHz. Each conversion takes 13 analog-to-digital clocks so

125 KHz /13 = 9615 Hz. Therefore, by using an arduino based microcontroller such as the Romeo board,

we were limited to a 9615Hz sample rate. This would provide us with about 16 samples at any single

point for a baseball of 2.9in in diameter moving at 100mph, a speed we never hoped to reach. This

showed that the board would not be a bottleneck. The second concern was the cost. The Romeo board

costs $29.99 for many features not required for this project. Buying a generic “Arduino” Nano board on

ebay (~$2) would accomplish the same tasks, but the Romeo board was more convenient for prototyping.

While the parts were being gathered, the circuit was designed. The initial design was to to run the

laser diodes out of a voltage regulator to avoid burnouts, because the lasers were low quality. Then each

photoresistor would connect to a transistor that would then connect to an or-gate, and finally to a digital

pin of the Romeo board. However, we realized a much simpler circuit could designed with only the

resistors and laser diodes.

By running the photoresistors in series, we could avoid the need for an or gate. This works

because the resistance increases by several orders of magnitude when not exposed to light. Then by using

the photoresistors like the emitter of a transistor, an output voltage can be read from the difference

between a reference resistance and the photoresistors. This removed the need for transistors. The Romeo

board is equipped with a series of analog ports that can be used as the input for this signal. Finally the

voltage regulator can be avoided by undervolting the laser diodes in parallel, which will slightly diminish

the intensity of the laser, but also avoid blowouts or fluctuations from the cheap diodes. The difference in

intensity turned out to be negligible for the photoresistors used. There is a 3.3V pin on the Romeo board,

so we did not need to make a voltage divider. This gave us a final circuit design with minimal cost and a

more precise and efficient output than originally conceived.

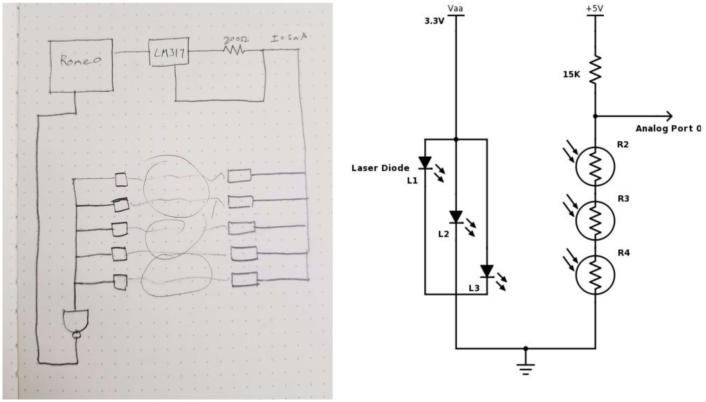
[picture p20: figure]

Figure 18. The first draft of the speedgate system vs a final circuit design

To prove the functionality of the system, the system was first developed on a breadboard and

powered off of a laptop. The code was written in the Arduino IDE. This allowed for a member to code

and debug while the mechanical system was being finalized by the rest of the team.

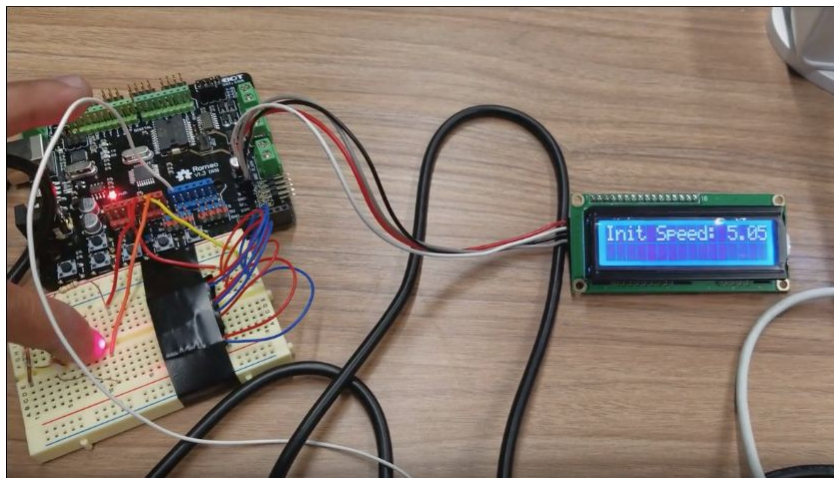
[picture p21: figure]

Figure 19. Test bench for LCD and Speedgate. The speed was found by breaking the laser with a finger.

The romeo board could be powered from any USB power supply that can output 6-23V. For

testing, the system was connected to a laptop, but can be connected to a cheap cellphone charger as we

did for demonstration. This increases portability, lowers cost and is more than enough to power the board,

lasers, and LCD.

The final issue was debugging the code. At speeds below 50mph, the system had no problem with

measurements. Both the inbound and outbound speeds and COR were consistent. Above 50mph, some of

the tests would result in extremely high readings upwards of 2000mph, if any reading at all. This was

because the code was originally designed to output the inbound speed before measuring the outbound

speed, meaning that the microcontroller had to run the calculations for the first speed before taking the

next reading. By moving all calculations to the end of the program, the system was able to accurately test up to 68.10mph. This could probably be made even more precise by utilizing photodiodes instead of

photoresistors.

V. | Data
| As a user interface feature, we introduced the ability for the user to ask for a desired inbound

speed of the baseball. To achieve this sort of feature, we needed to empirically determine what chamber

pressures led to what inbound velocities. At the request of the user, the microcontroller could then output

a recommended pressure for the chamber. Below in Fig. 19 are three empirical curves we used to

implement this speed selection feature.

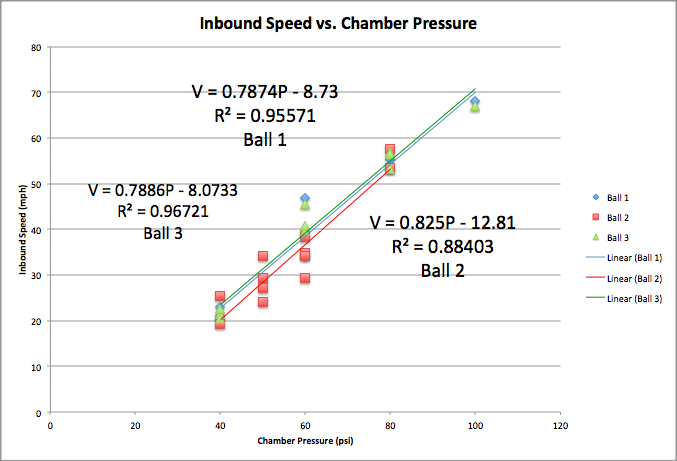
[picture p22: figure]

| Figure | 20. Empirical relationship for inbound speed versus chamber pressure for two different baseballs.

Not surprisingly, the three datasets for the two different balls yielded similar inbound speeds

given the same chamber pressure. When we implemented the speed selection feature in our

microcontroller, we simply inputted velocity, and used the above relations to get three values for chamber

pressure, and responded to the user with the average of the three chamber pressures. The user would then

pressurize the chamber with either a bike pump or compressor, and fire the cannon.

This next plot provides our answer to the task posed in the project description. Below is our best

attempt to quantify how the COR is related to the relative velocity between a baseball and a piece of

wood, or in our case, just the inbound velocity of the baseball.

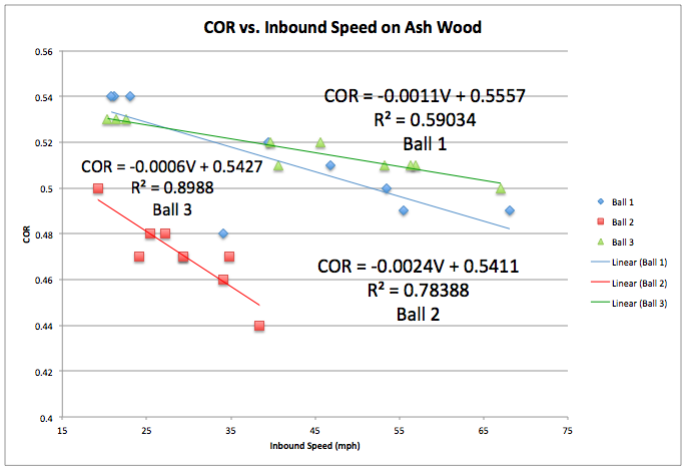
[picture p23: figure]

Figure 21. COR versus inbound speed. Basic linear fits applied to all sets of data. Uncertainty for values

of COR is 4%.

As Fig. 20 above demonstrates, the COR tends to decrease with an increase in inbound velocity.

We have attempted to apply linear fits to the data collected from ball 1, ball 2, and ball 3, but none of the

fits is very convincing. With more data points spread out across a bigger spread of velocities, applying a

mathematical model to the relationship between COR and inbound speed might be possible.

Major League Baseball rule 1.09 states “baseballs must register a rebound 54.6% of the original

velocity, plus or minus 3.2 percent” to be considered legal during an “ASTM standard wall test” (6). An

ASTM standard wall test constitutes shooting a ball from an air cannon perpendicularly towards a piece

of 2.5” thick, 12” wide, 12” tall white ash wood mounted to a steel plate at 60 mph (7). Looking at the

data points we have for ball 1 and ball 2 near 60 mph, the values for the COR do not fit within the 0.546

+- 0.032 range constituting a legal ball. This is illustrative, but not exactly damning. Our values for COR

at 53.51, 55.49, and 68.10 mph were 0.50, 0.49, and 0.49 respectively for ball 1, and at 56.97, 56.38, and

67.03 mph were 0.51, 0.51, and 0.50 respectively for ball 2. These values are very close to the range

identified by the MLB as “legal,” and they are also very consistent with one another. The very close

grouping of the COR values demonstrates either a systematic error in the system, induced by one or

multiple facets of our system, or perhaps that the balls we used were not legal. MLB baseballs are rolled

seam baseballs, and many baseballs fall out of the “legal” category with use due to wearing of leather and

stitching (7). The balls we used for testing were certainly not new, and were most likely not of MLB

quality or specifications. Since the balls we tested with are possibly, and are frankly likely, not legal

baseballs by MLB standards, it is not a fair metric to judge the efficacy of our system based on a the

tested baseballs falling within the “legal” criteria. To properly apply this judgement metric, we must

acquire some confirmed legal MLB baseballs, and run tests with them.

The Umass Lowell Baseball Research Center also performs COR testing using another method

other than the ASTM standard wall test. They use a machine called the Baum Hitting Machine. This machine facilitates a very controlled impact between a moving bat swinging at 90 mph and a baseball

moving at 70 mph. This test yielded an average COR of 0.506 in 1999 and 0.503 in 2000. These literature

COR values are much closer to the values we reported for ball 1, ball 2, and ball 3. Umass Lowell offers

an explanation that begins to make sense of our results. When describing the differences in COR between

the ASTM standard wall test and the Baum Hitting Machine tests, Umass Lowell states “the wall method

impacts the ball against a flat wall, while the hitting machine impacts the ball against a wood bat—a solid

cylinder. The geometrical differences between the wall and the cylinder influence the ball deformation.

The wall flattens the ball more than the bat does, and the bat allows the ball to wrap around the barrel.

Second, the wall test uses a ball speed of approximately 60 mph impacting a stationary wall, while the

hitting machine has a ball pitch of 70 mph impacting a bat swinging at 90 mph (the 90 mph is at the tip of

the bat and this tip speed corresponds to 70 mph at the point of contact on the bat, which is 6 inches from

the tip of the barrel). The ball deformation is a nonlinear phenomenon. Therefore, it is not unexpected

that the COR’s between the two testing methods differ.” Although we cannot argue that the relative

impact speed in the ASTM wall test is far more similar to our experimental system than the collision

speed facilitated by the Baum Hitting Machine, the geometry of the collision in our system is more

similar to the Baum Hitting Machine test. The piece of wood that the baseball collides with in our system

is only 1.5” in height. Since the diameter of a baseball is 2.9”, during the collision, the baseball will

experience a similar wrapping effect around the piece of wood that is observed in the Baum Hitting

Machine tests. Understanding this important similarity, and further acknowledging the consistency with

which our system calculates COR values, we argue that our system compares more favorably to the Baum

Hitting Machine than the ASTM wall test. While we cannot reconcile the significant difference in relative

collision speed between the wood and the baseball between the Baum Hitting Machine and our system,

the similar geometry of deformation and similar COR values our system yields to Umass Lowell suggests

that our system is certainly effective for determining an accurate COR. Additionally, after applying our uncertainty assignment (plus or minus 4%) to our COR values, the spread of possible values completely

encapsulates the values presented from the Baum Hitting Machine tests, and comes closer to the values

yielded from the ASTM wall test.

The correlative trend in the COR data (as impact velocity increases, COR decreases) also

compares favorably to professional publications. Reports from the Umass Lowell Baseball Research

Center confirm the same correlative trend, but similarly struggle to apply a mathematical model to the

relationship. However, it is evident that the relationship is not linear, but more of a decay to some

threshold COR value at speeds in excess of 120 mph (7).

VI. | Potential | Future | Work/Scalability

There were some features that our team wanted to incorporate, however because of time and

money restrictions, we weren’t able to. When thinking of scalability and potential future designs, we

thought of a many different ways we could improve our system. In order to increase the ease of use of our

air cannon, we wanted to remove the human input of pumping the bike pump and simply add an electric

compressor to pressurize the chamber quickly and with less effort. Ideally, the desired initial speed would

be inputted and the approximate psi value of the chamber would be outputted on the LCD. The system

would then automatically start the compressor until the desired psi is attained and would automatically

shut off the compressor.

We additionally want to modify the speedgate to be more precise, flexible, and cheaper. With the

use of the Trinity Engineering 3D printers, we can print a speedgate of the same width to include two

grids of lasers with a difference in width known to 0.1mm. This would guarantee near perfect alignment,

with both grids contained by the same rigid structure to avoid interference. This allows for velocities to be

measured without assuming the diameter, and solves all the potential disadvantages of the two point

system described earlier. The photoresistors with a 10msec response time would be replaced with photodiodes of a 20nsec response time to improve the precision of the gate. This will allow the sensors to

be take full advantage of the 9600Hz sample rate on the Arduino board of choice. In this case, the arduino

board should be a generic clone of the Arduino Nano, which we have found for as low as $2 from various

retailers.

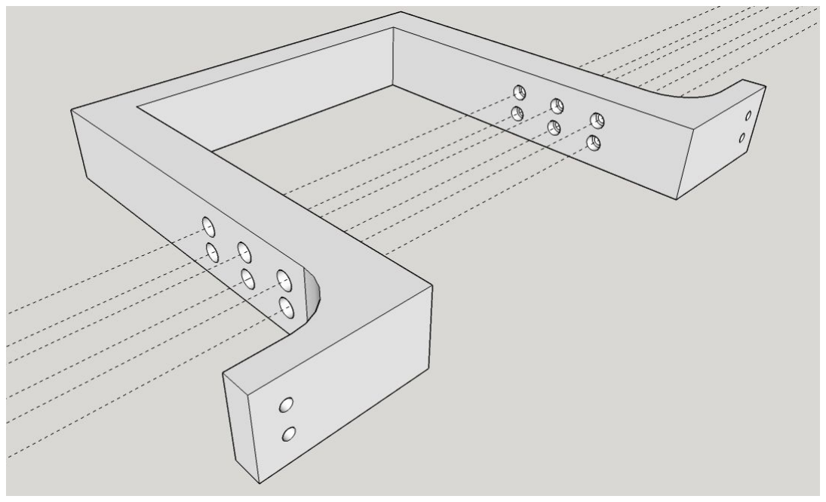
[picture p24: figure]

Figure 22. An improved speedgate design, tall enough to let the collision tube move freely, with two

planes of measurement and added screw holes for permanent mounting to the system.

VII. | Concluding | Remarks | and | Acknowledgements

Let us restate the definition of the central task: “to design and construct a system to reliably and

accurately determine the COR of a baseball with a piece of wood as a function of the relative velocity

between the two bodies.” Per this definition, we conclude that our design was successful. We delivered a

reliable, accurate, and easy to use system that resolved COR values for baseballs within the ranges

presented by Umass Lowell for the Baum Hitting Machine test. Given more time, money, and resources,

we would perform more extensive testing with official MLB quality baseballs to further inquire about our

system’s efficacy. We also would add more ease of use features to make the system more marketable.

This project was both challenging and an excellent test of collaboration. We attribute the efficacy

of our design to considerable thought, planning, and playing to the strengths of our team members.

We would like to acknowledge the YouTube channel Making Random for help in constructing

the air cannon. We also would like to acknowledge Andrew Musulin for extensive help with acquiring

materials and assembling the system. Finally, we would like to acknowledge Prof. Mertens and Prof.

Fixel for guidance along the way.

VIII. | Bill | of | Materials
Table | 2. Tabled materials and component list
Item | Subsystem | Price ($) | Quantity | Total ($)
Irritrol Sprinkler Valve | Air Cannon | 24.89 | 1 | 24.89
Air Gun Valve | Air Cannon | 7.85 | 1 | 7.85
1” Male PVC Adaptor | Air Cannon | 0.74 | 3 | 2.22
1” PVC Elbow | Air Cannon | 1.09 | 2 | 2.18
4”x3” Reducing PVC Couple | Air Cannon | 6.72 | 1 | 6.72
1”-11/2” Flush Bushing | Air Cannon | 3.70 | 2 | 7.40
3” PVC Coupling | Air Cannon | 1.43 | 1 | 1.43
Bike Pump | Air Cannon | 19.96 | 1 | 19.96
Ash Wood | Collision Tube | 10.00 | 1 | 10.00
Mini Laser Diode 650nm | Speed Gate | 0.60 | 3 | 1.80

Table | 3. Borrowed or scavenged parts
Item | Subsystem | Est. Price ($) | Quantity | Total ($)
PVC Components | Cannon | 15.00 | 1 | 15.00
DFRobot Romeo | Speed Gate | 30.00 | 1 | 30.00
3D printed part | Speed Gate | 5.00 | 1 | 5.00
Photoresistor | Speed Gate | 0.05 | 3 | 0.15
Wires | Speed Gate | 0.10 | 1 | 0.10
IX. | References
1. “Air Cannon vs. 27" Tube TV Slow Motion Video.”
| https://www.youtube.com/watch?v=aK9Y_kVU59A
2. Nathan, Alan M. et al. “Spin of a Batted Baseball.” 9th Conference of the International Sports
| Engineering Association. Procedia Engineering. 29 February 2012.
| http://baseball.physics.illinois.edu/ProcediaEngineering34Spin.pdf
3. “Spin Rate: What We Know Now.” Driveline Baseball.
| https://www.drivelinebaseball.com/2016/11/spin-rate-what-we-know-now/
4. Fitt, Aaron. “NCAA To Switch to Flat Seamed Balls in 2015.” 06 November 2013.
| http://www.baseballamerica.com/college/ncaa-to-switch-to-flat-seamed-balls-in-2015/#G6uAm6
| p1zyMpZ2JV.97 (http://www.baseballamerica.com/college/ncaa-to-switch-to-flat-seamed-balls-in-2015/)
5. “The Complete Guide to Baseballs.”
| http://protips.dickssportinggoods.com/sports-and-activities/baseball/how-to-buy-baseballs
6. Major League Baseball Rules Project. http://mlbrulesproject.blogspot.com/2012/05/rule-109.html
7. Umass Lowell Baseball Research Center. Performance Comparison of the 1999 and 2000 Major
| League Baseballs. 27 June 2000.

8. Cross, Rodney. Physics of baseball & softball. Springer, 2011.
X. | Appendix
Table | 4. Raw Data, Ball 1.
Pressure (psi) | V1 (mph) | V2 (mph) | COR
40 | 21.1 | 11.35 | 0.54
40 | 20.81 | 11.27 | 0.54
40 | 23.05 | 12.49 | 0.54
60 | 39.43 | 20.52 | 0.52
60 | 34.05 | 16.46 | 0.48
60 | 46.82 | 23.78 | 0.51
80 | 53.51 | 26.75 | 0.50
80 | 55.49 | 27.24 | 0.49
100 | 68.1 | 33.29 | 0.49
Table | 5. Raw Data, Ball 2
Pressure (psi) | V1 (mph) | V2 (mph) | COR
40 | 19.21 | 9.67 | 0.50
40 | 25.39 | 12.28 | 0.48
50 | 27.24 | 13.03 | 0.48
50 | 29.38 | 13.75 | 0.47
50 | 24.17 | 11.44 | 0.47
50 | 34.05 | 15.61 | 0.46
60 | 38.42 | 16.83 | 0.44

60 | 29.38 | 13.75 | 0.47
60 | 34.84 | 16.46 | 0.47
Table | 6. Raw Data, Ball 3
Pressure (psi) | V1 (mph) | V2 (mph) | COR
40 | 21.42 | 11.44 | 0.53
40 | 20.37 | 10.76 | 0.53
40 | 22.61 | 12.07 | 0.53
60 | 39.66 | 20.51 | 0.52
60 | 40.70 | 20.92 | 0.51
60 | 45.65 | 23.58 | 0.52
80 | 56.97 | 28.83 | 0.51
80 | 53.21 | 26.99 | 0.51
80 | 56.38 | 28.54 | 0.51
100 | 67.03 | 33.42 | 0.50

Code

/*
Coefficient of Restitution Test System
Written by Adam Woo

This program was designed to use a laser diode array to identify when a baseball has entered and left a single plane, giving the velocity of the object perpendicular to the plane. The program will then analyse the restitution properties of the object ball by comparing the initial and rebound velocity. All data will be displayed on a 2x16 character LCD.
*/

/*----------------------------------------------------------------------------include libraries
*/----------------------------------------------------------------------------

#include <Wire.h>

#include <LiquidCrystal_I2C.h>

LiquidCrystal_I2C lcd (0x20,16,2);

/*----------------------------------------------------------------------------define constants and variables */----------------------------------------------------------------------------#define baseball_diameter 75 //millimeters
#define milliPerMicro_to_milePreHour 2237.4145431945

int NUM_BUTTON = 3;
int adc_key_val[5] ={30, 150, 360, 535, 760};
int buttonPin = 7; // choose the input pin (for pushbutton) int button;
int stage = 0; | // variable for stage of testing
int mph = 0; | // variable for setting MPH
int psi;
int photocellPin = 0; // the cell and 15K pulldown are connected to a0 int tests;
int buttonPress;
unsigned long SensorOne_timerIn;
unsigned long SensorOne_timerOut; double timePlaneOne;
double speedIn;
unsigned long SensorTwo_timerIn; unsigned long SensorTwo_timerOut; double timePlaneTwo;
double speedOut;
double COR;

void setup(){
/*----------------------------------------------------------------------------initialize LCD and photoresistor pin */----------------------------------------------------------------------------lcd.init ();
lcd.backlight ();
lcd.begin(16,2);
pinMode(photocellPin, INPUT); | // declare speed gate as analog input
Serial.begin(9600);
}

void loop(){
while (stage == 0){
/*----------------------------------------------------------------------------push buttons select the desired mph to display the needed PSI, then activates the speedgate for measurement. Allows for measurement system to ignore loading. */----------------------------------------------------------------------------

set(button);
if (button !=0){
delay(400);
}
buttonPress = analogRead(buttonPin); | // read the value from the sensor
button = get_button(buttonPress); | // convert into key press
}

while (stage == 1){
/*----------------------------------------------------------------------------all measurement take place in the "measure" function */----------------------------------------------------------------------------measure();
}

while (stage == 2){
/*----------------------------------------------------------------------------a ll calculations and printing done after all measurements */----------------------------------------------------------------------------timePlaneOne = (SensorOne_timerOut-SensorOne_timerIn);
speedIn = (baseball_diameter/timePlaneOne)*milliPerMicro_to_milePreHour; timePlaneTwo = (SensorTwo_timerOut-SensorTwo_timerIn);
speedOut = (baseball_diameter/timePlaneTwo)*milliPerMicro_to_milePreHour;

lcd.clear();
lcd.setCursor(0,0);
lcd.print("V1:");
lcd.setCursor(0,1);
lcd.print(speedIn);
// | Serial.println(timePlaneOne); | test
// | Serial.println(speedIn);
| lcd.setCursor(6,0);
| lcd.print("V2:");
| lcd.setCursor(6,1);
| lcd.print(speedOut);
// | Serial.println(timePlaneTwo);
// | Serial.println(speedOut);
| COR=speedOut/speedIn;
// | Serial.println(COR);
| lcd.setCursor(12,0);
| lcd.print("COR:");
| lcd.setCursor(12,1);
| lcd.print(COR);
| while (COR!=0){}
}
}

void set(int action){
if(action==1){
| mph = mph + 10;
if (mph > 70){ | // resets desired mph after 70mph because faster speeds
require dangerous PSI
| mph = 0;
| lcd.clear();
}
}
else if(action==2){
stage = 1; | // moves to measure stage

}

psi = round((1.2*mph)+13); // PSI calculations found by data generated empirical curve

lcd.setCursor(0,0);
lcd.print("Desired MPH: ");
lcd.print(mph);
lcd.setCursor(0,1);
lcd.print("Desired PSI: "); lcd.print(psi);
}

void measure(){
/*----------------------------------------------------------------------------loops if nothing has passed though the speed gate */----------------------------------------------------------------------------if (tests == 0){
lcd.clear();
lcd.setCursor(0,0);
lcd.print("Ready for test");
tests = 1;
}

while (analogRead(photocellPin)<60){} // while grid unbroken do nothing

if (tests == 1){
/*----------------------------------------------------------------------------first measurement
*/----------------------------------------------------------------------------SensorOne_timerIn = micros(); //record the time the ball reaches the gate first time
while (analogRead(photocellPin)>60){} // while grid is broken do nothing SensorOne_timerOut = micros();
// | Serial.println(SensorOne_timerIn); | testing
// | Serial.println(SensorOne_timerOut);
tests = 2; | // initiate outbound measurement
}

else if (tests == 2){
/*----------------------------------------------------------------------------second measurement
*/----------------------------------------------------------------------------SensorTwo_timerIn = micros(); //record the time the ball reaches the first gate
| while (analogRead(photocellPin)>60){}
| SensorTwo_timerOut = micros();
// | Serial.println(SensorTwo_timerIn);
// | Serial.println(SensorTwo_timerOut);

tests = 3;
stage = 2;
}
}

int get_button(unsigned int input){ /*----------------------------------------------------------------------------checks which button has been pressed (not needed if using external buttons) */----------------------------------------------------------------------------int k;
for (k = 0; k < NUM_BUTTON; k++){
if (input < adc_key_val[k]){
return k;
}
}
if (k >= NUM_BUTTON){
k = 0; // No valid key pressed }
return k;
}

Meeting Minutes

Meeting | 1: | 09/07/2017 | 12:45pm-1:30pm_Recorded | by | Dana | Wensberg
Meeting:
- Brainstorming: how are we getting the ball moving?
- dropping it
- ramp
- chris sale
- how are we measuring energy prior to impact
- speed gate
- potential energy calculation
- how are we measuring after
- bouncing up and measuring height
- speed gate on the way out
- spring system like a pez dispenser
- types of wood, what types, baseball applications
- bike pump solenoid shooting system
- butterfly valve
- getting it going
- https://www.youtube.com/watch?v=PTh9XtshPIg
- pvc air cannon, two staged, butterfly valve in between, analog/digital pressure tap in pressure chamber with insulated one way check valve for bike pump filling
- probably need a custom adaptor for the transition
- massive spring slingshot that catches ball
Meeting | 2: | 09/11/2017 | 6:00pm-8:15pm_Recorded | by | Mariam | Avagyan

People Present: everyone
Updates: We have not decided on a final design yet. Meeting:
- Recap of previous ideas
- We will use a net to catch the ball after collision
- Research on COR needs to be done to find out about the wood surface that the ball is bouncing off of and whether or not we can allow the board to flex.
- Adam suggested a new idea: we have two speed gates. Fire a ball and block of wood at each other with the same relative momentum, they collide in a PVC pipe. Benefits: this design is closer to the real-life designs.
- We can’t put anything on the balls (such as accelerometer) to measure speed since it will change the COR.
- Compressor: http://www.homedepot.com/p/Husky-120-Volt-Inflator-HY120/202871788
- Questions to ask to Prof. Mertens: would a bike pump, PVC, and other components in the system count for Ease of Use points because they can be used in everyday life for other applications?
- Consensus: we will use an air cannon to move the ball. We will use a speed gate (we will borrow one or build it). Either way, we will include “How To Build Your Own Speed Gate” in our report.
- We can use a phone camera and use image processing to measure velocity and position of collision. Cons: will make the design bigger, will lower ease of use.
- We can have the ball stationary, everything else would be moving.
- We can put something inside horizontally the PVC pipe to measure the speed (lasers, magnets…)
- Why can we use a speed gate and not a radar gun?
- Wood is hanging, the ball hits it. We measure how much the wood swung back. That’s how we measure energy transfer.
- Wood is connected to a spring which is connected to the wall. The ball hits the wood and we measure the spring compression. Cons: realistic applications, reliability.
- We decided to spend most of the budget on things that will help us make better (precise and accurate) measurements.
- Let’s use PASCO for a speed gate?
- Another idea: swing a baseball bat down, time it with the cannon. Consistency might be an issue.
- Create a mechanical arm that spins the ball and lets who when it’s vertical. Use rpms to find the speed.
- We can have the wood with a less diameter than our PVC pipe. When the ball hits the wood, the air will have room to escape.
- Make a solenoid, railgun?
- Have two strings, pull carts
- https://www.pasco.com/prodCatalog/ME/ME-9259_laser-switch/
- http://archive.iorodeo.com/content/large-physics-photogate
Next | meeting: | Thursday Sept 14, 4:30-6:30pm
Assigned | Tasks: | Things we need to do before the next meeting:
- Adam will talk to Prof. Mertens
- Mariam will talk to Prof. Fixel and Prof. Huang
- Dana will look into components we need for the air cannon

- Brayan can start the design report outline if he has time but it’s not urgent. Goals: by the end of the week we want the design chosen.
Meeting | 3: | 09/14/2017 | 4:30pm-6:00pm_Recorded | by | Brayan | Duarte
Updates: We scavenged for items and found 4” and 3” PVC pipes, one 1” 90 degree bend, and 4” pipe end.
Meeting:
-After scavenging, we’re finalizing the plan and seeing what else it is that we need
Things we still need:
- Bike pump fitting
- 4” - 1” pipe “converter?”
- Quick release, 1” female both sides
- Paste stuff
- Valve
- Drill
- Air blow gun ($7.85 on amazon prime)
Assigned tasks:
-Adam, Mariam, and Brayan will go to Home Depot on 09/14/2017
Meeting | 4: | 09/15/2017 | 4:30pm-6:00pm_Recorded | by | Mariam | Avagyan
Updates: We cut the PVC pipe in the woodshop.
Next | Meeting: | 09/16/2017
Meeting | 5: | 09/16/2017 | 10:00am-1:00pm_Recorded | by | Mariam | Avagyan
People | present: everyone
Meeting:We are going to Home Depot to buy the following items.
- Quick Release mechanism, quick release trigger
- Bike pump, adapter, schrader valve
- 4’ to inlet, outlet to 3’
- PVC cement, primer, high pressure rated epoxy
- Teflon tape
Updates: - Did not buy anything from Home Depot. Ordered stuff on Amazon.
- Need or order pipe connections on Amazon
- Decided to build a speed gate ourselves.
Assigned tasks:
- Adam and Mariam will make the speed gate (3D print, get photoresistors from Andrew)
- Dana and Brayan will find everything needed for the air cannon

*NOTE: After September 16th, we divided work among ourselves and met numerous times. Meeting minutes were not recorded at these meetings.

Tasks | during | this | period:
Dana & Brayan - Assemble Air Cannon
Adam - Model and print speed gate; code, build, and test circuit on breadboard Mariam & Adam - Assemble speed gate

Meeting: | 9/29/2017 | 3:00pm-5:00pm
People | present: Dana, Adam
Meeting: | - Dana and Adam built system platform in woodshop
Updates: - Electrical System finished and ready for implementation
Meeting: | 9/30/2017 | 8:00pm-10:00pm
People | present: Dana, Adam, Mariam
Meeting: | - Mounted speedgate
- Did testing, gathered data.
Updates: - Brayan bought a USB power bank to use for demonstration day
Meeting: | 10/1/2017 | 6:00pm-9:00pm
People | present: Dana, Adam
Meeting: | - Debugging and troubleshooting
- Did testing, gathered data.

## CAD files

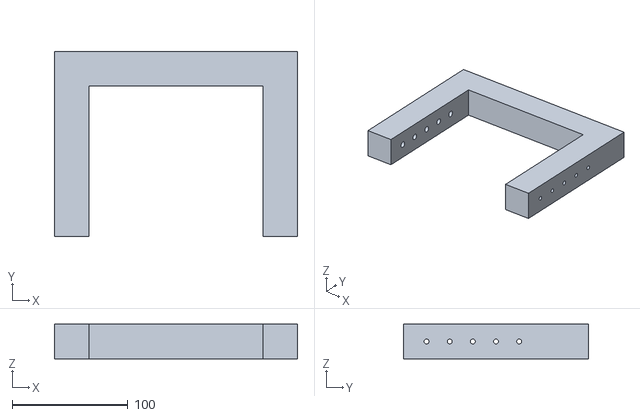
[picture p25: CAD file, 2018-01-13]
Speed_Gate/CAD_models/Speed Gate v1.0.stl
210.0 x 160.0 x 30.0

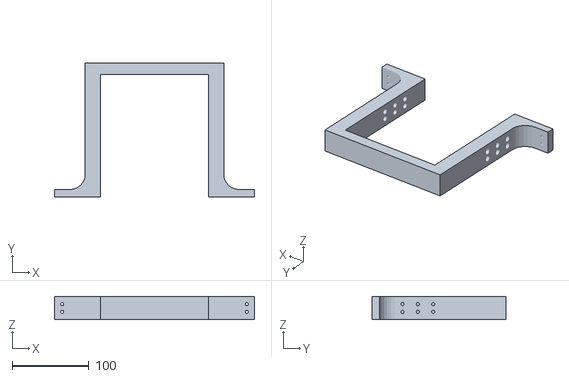
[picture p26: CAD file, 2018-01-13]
Speed_Gate/CAD_models/Speed Gate v2.0.stl
260.2 x 175.0 x 30.0
